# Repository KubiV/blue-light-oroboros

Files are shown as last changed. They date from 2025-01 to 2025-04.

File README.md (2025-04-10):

# blue-light-oroboros

## Úvod
V této práci se zabýváme vývojem externího světelného LED zdroje pro přístroj Oroboros O2k, který slouží pro vysoce přesné monitorování respirační aktivity biologických a biochemických vzorků.

Aplikace pro ovládání LED
*Stroj Oroboros O2k s nasazeným světlem*

## Problém
Stávající světelné zdroje pro Oroboros O2k jsou drahé a u starších modelů již nedostupné. Naším cílem bylo navrhnout cenově dostupnou a modulární alternativu, která by umožnila precizní experimentální podmínky.

## Materiál a metody
Náš systém zahrnuje řídící box s elektronikou založenou na Arduino Leonardo. K ovládání světel je použit rotační enkodér a 3 tlačítka, zatímco desktopová aplikace umožňuje softwarové nastavení PWM signálu (0–255) pro dvě LED diody. LED zdroje s dominantní vlnovou délkou 465 nm jsou integrovány do 3D tištěných pouzder. Experiment proběhl s bilirubinem rozpuštěným v BSA, kdy fotooxidační reakce bilirubinu (na lumirubin a biliverdinové deriváty) vedly k měření spotřeby kyslíku.

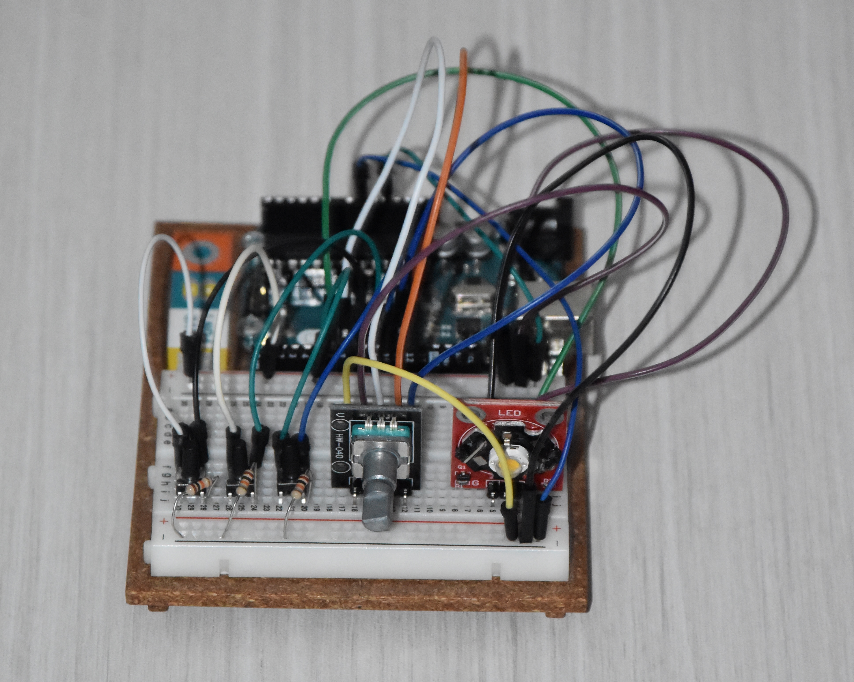
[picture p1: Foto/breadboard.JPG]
První prototyp

*První verze zapojení na nepájivém poli*

Protodeska
*Finální zapojení na prototypové desce*

## Technický popis
Projekt využívá Arduino Leonardo pro řízení dvou LED diod, s PWM regulací a jednoduchým ovládáním pomocí enkodéru a tlačítek. Firmware na řídícím čipu přijímá sériové příkazy pro nastavení jasu jednotlivých LED. Uživatelská aplikace, vyvinutá v Pythonu s knihovnou PyQt5, umožňuje ovládání LED přes grafické rozhraní se samostatnými i synchronizovanými časovači, sliderem a textovým vstupem. Modularita hardwaru umožňuje rozšíření o další zdroje s různými vlnovými délkami.

Finální box
*Finální box s možností připojení dvou LED světel*

## Výsledky
Vyvinutý systém umožňuje individuální i synchronizované ovládání obou LED světel, včetně časovačů pro přesné nastavení trvání osvětlení. Software poskytuje interaktivní slider, tlačítka předvoleb a možnost zadat konkrétní hodnoty jasu, což vede ke spolehlivému monitorování spotřeby kyslíku a k analýze fotoproduktů.

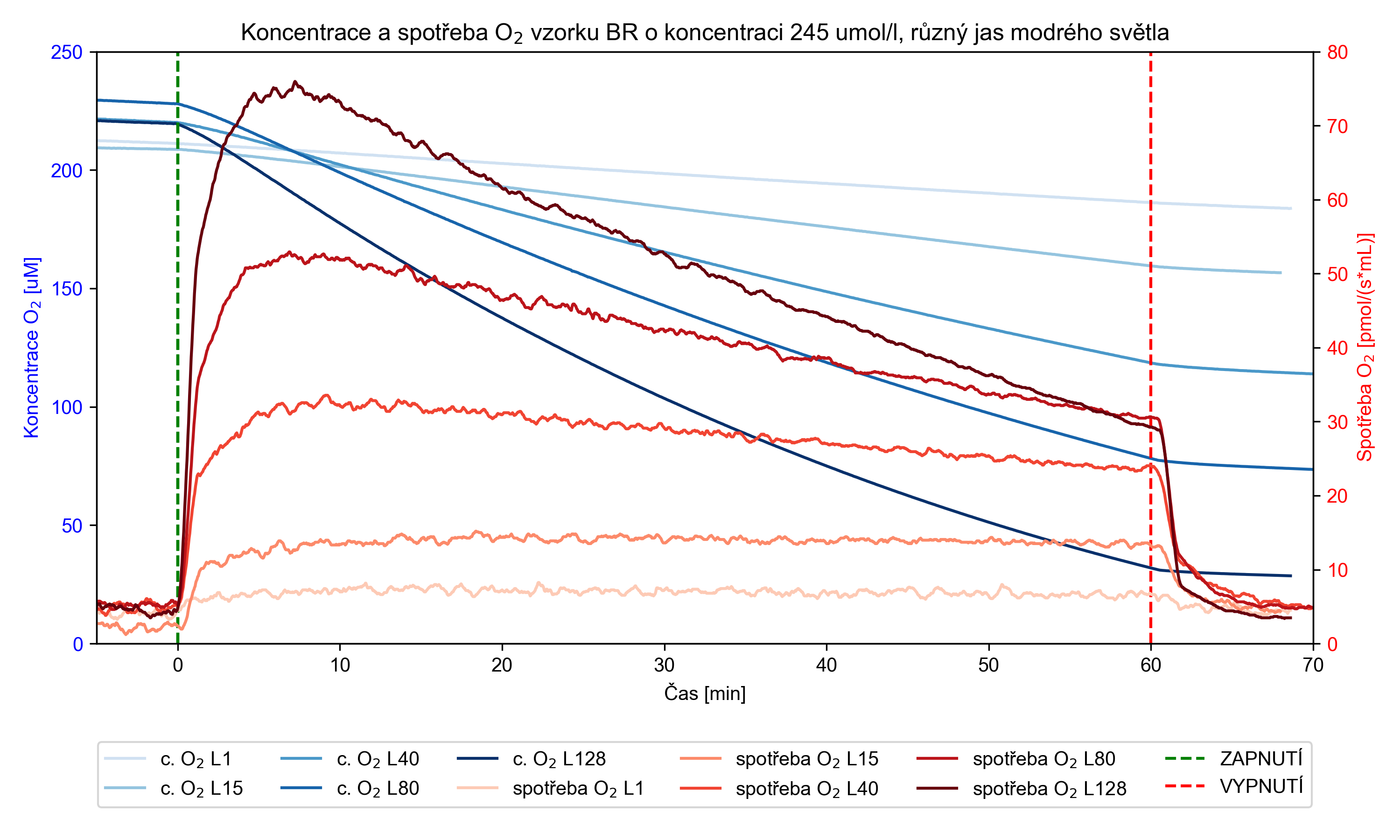
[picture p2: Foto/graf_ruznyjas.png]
Různý jas světla

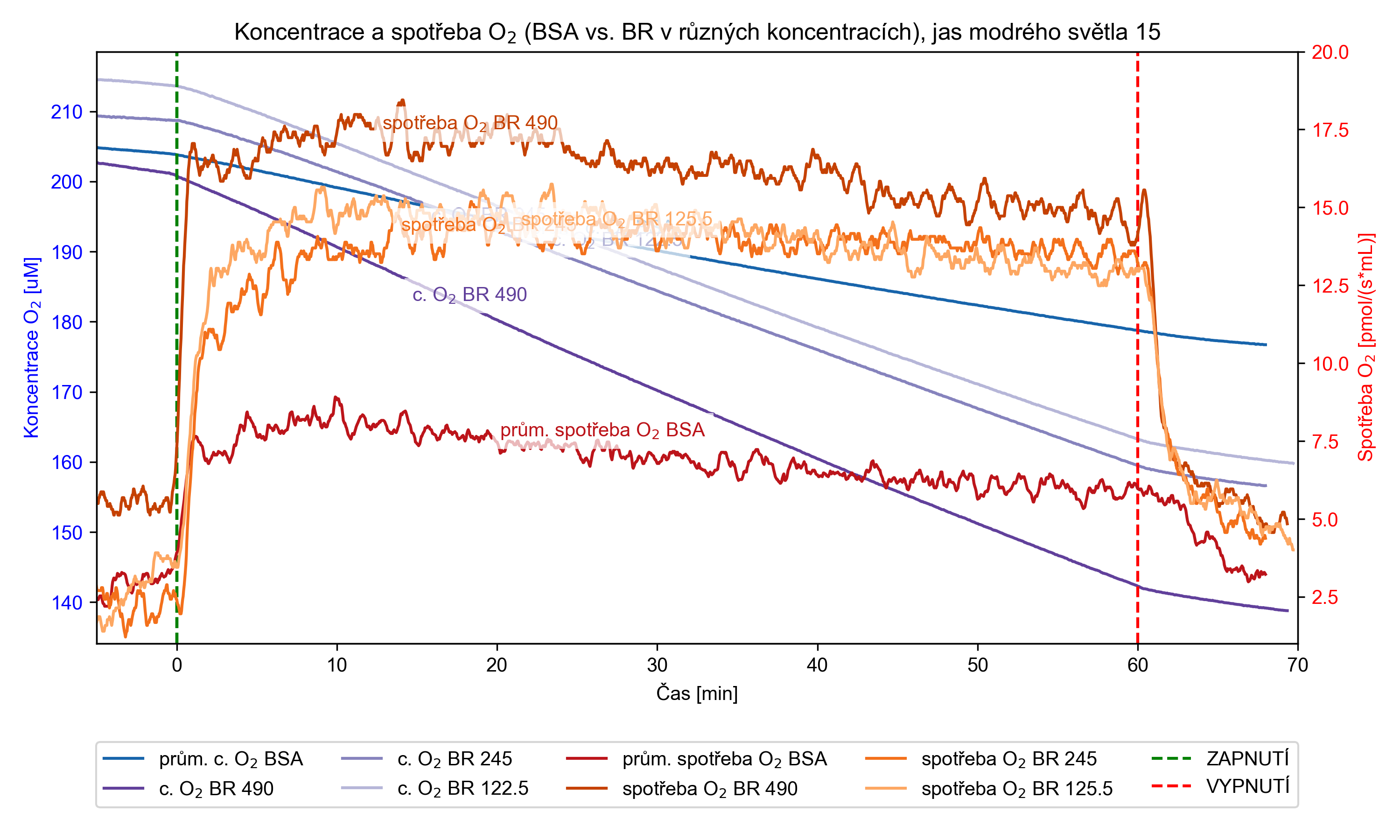
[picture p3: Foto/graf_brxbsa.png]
Různé koncentrace BR

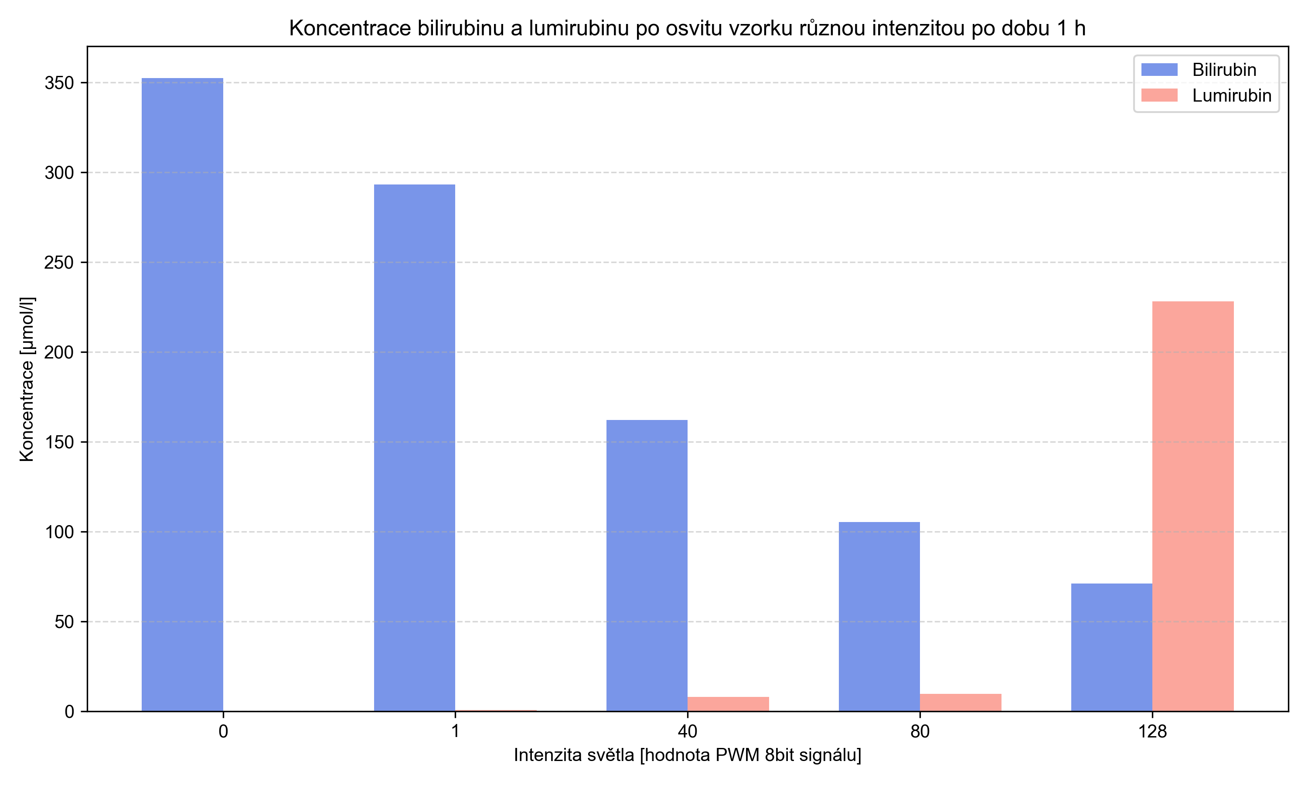
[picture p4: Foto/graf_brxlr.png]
Koncentrace BR a LR

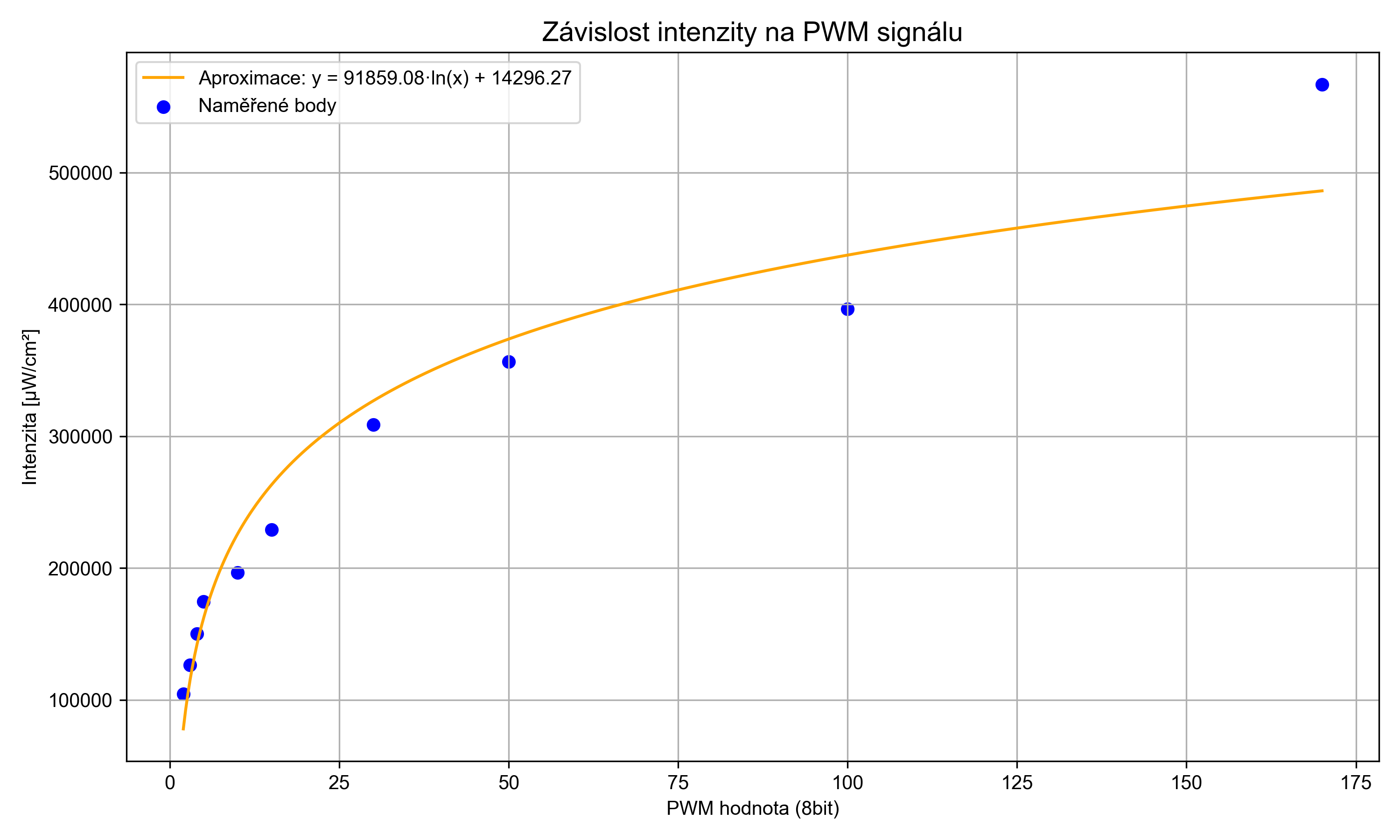
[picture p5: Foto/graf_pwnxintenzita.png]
Intenzita a PWM světelného zdroje


## Závěr a diskuse
Náš LED zdroj představuje praktickou a ekonomickou alternativu k původním řešením. Jeho modularita umožňuje rozšíření o další světelné zdroje s různými vlnovými délkami. Experiment s bilirubinem ukázal, že naše řešení umožňuje precizní kontrolu osvětlení, což výrazně ovlivňuje experimentální podmínky a kvalitu dat.

## Technická dokumentace

### Struktura projektu
```
blue-light-oroboros/
├── requirements.txt         # Seznam závislostí pro Python aplikaci a generování grafů
├── Software/
│   └── SW_Dual/
│       ├── led/
│       │   └── led.ino      # Arduino firmware pro ovládání LED
│       └── led2.py          # Python aplikace pro ovládání LED
├── Data/
│   ├── Graph1/
│   │   └── graph4.py        # Vizualizace dat - koncentrace BR
│   ├── Graph2/
│   │   └── graph1.py        # Vizualizace dat - různé intenzity světla
│   ├── Graph3/
│   │   └── graph1.py        # Vizualizace dat - porovnání BR a LR v různých vzorcích
│   └── Graph4/
│       └── graph1.py        # Vizualizace dat - závislost intenzity a PWM
├── CAD/
│   ├── 3D print/
│   │   └── BlueLight.3mf    # Detaily pro tisk ve formátu 3MF (LED světlo)
│   └── BlueLight.step       # Zdrojový STEP soubor pro 3D model (LED světlo)
└── Docs/
  └── Instrukce.pdf          # Instrukce pro sestavení kryu LED světla
```

### Popis komponent

#### Arduino Firmware (led.ino)
- Ovládání dvou LED zdrojů přes PWM (piny 11 a 3)
- Implementace rotačního enkodéru pro manuální ovládání jasu
- Tři tlačítka pro rychlé předvolby (vypnuto, přepínání LED, maximum)
- Sériová komunikace pro příjem příkazů z PC aplikace

#### Python Aplikace (led2.py)
- GUI aplikace vytvořená v PyQt5
- Ovládání jasu LED pomocí slideru nebo přímého zadání hodnoty
- Implementace časovačů pro každou LED
- Možnost synchronizace obou LED
- Sériová komunikace s Arduino kontrolérem

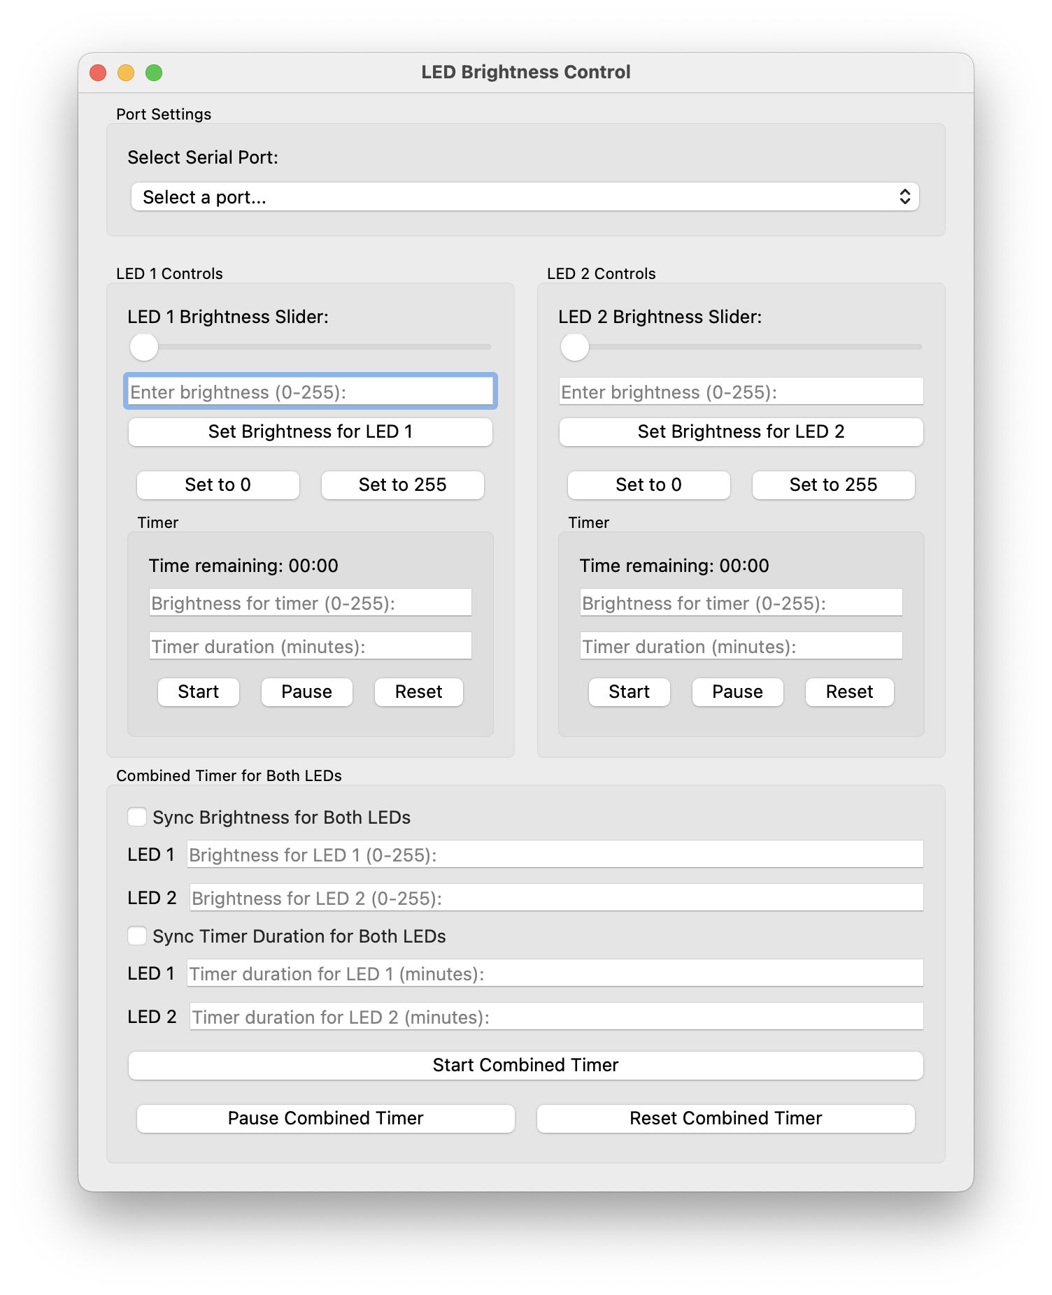
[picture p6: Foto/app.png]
Detail aplikace

*Uživatelské rozhraní aplikace pro ovládání LED světel*

#### Vizualizační skripty
- **graph1.py**: Analýza a vizualizace dat pro různé intenzity osvětlení
- **graph4.py**: Analýza a vizualizace dat pro různé koncentrace bilirubinu

### Hardware
- Arduino Leonardo
- 2x LED dioda (465 nm)
- Rotační enkodér
- 3x tlačítko
- 3D tištěná pouzdra pro LED a řídící box

### Komunikační protokol
- **Příkazy pro Arduino:**
  - `SET1:xxx` - Nastavení jasu LED 1 (xxx = 0-255)
  - `SET2:xxx` - Nastavení jasu LED 2 (xxx = 0-255)
- **Odpovědi z Arduina:**
  - `BRIGHTNESS1:xxx` - Aktuální jas LED 1
  - `BRIGHTNESS2:xxx` - Aktuální jas LED 2

## Literatura
- Oroboros Instruments: https://wiki.oroboros.at/index.php/PB_Light_Source
- Nature Article: https://www.nature.com/articles/s41598-020-61280-z
- Pediatrics: https://publications.aap.org/pediatrics/article/114/1/297/64771/Management-of-Hyperbilirubinemia-in-the-Newborn?autologincheck=redirected

## Poděkování
Děkujeme všem, kteří přispěli svými odbornými znalostmi a podporou k úspěšnému vývoji tohoto projektu.

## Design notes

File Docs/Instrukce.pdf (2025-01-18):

## Sestavení DriverBoxu

1) 3D tisk součástek
- Box
- Cover
- Knob
2) Shromáždění komponent
- LED driver board
- Arduino UNO/Leonardo
- USB kabel
- Rotary encoder
- 3x button
- 3x Rezistor (10 kOhm)
- Kablíky
- Proofboard
- Pinová lišta
- Delší 2 kabely (+ konektor)
- Nejméně 2x M3 matka a šroubek
- Smršťovací bužírky
- Stahovací pásky/lepidlo
3) Stavba obvodu proofboard jako shield desky k Arduino UNO/Leonardo (dle schématu)
4) Usazení shieldu na Arduino plus přidání podpěry kvůli stabilitě při stisku tlačítek
5) Vložení elektroniky do boxu a přišroubování
6) Zavření víka boxu
7) Nasazení knobu na rotary encoder
8) Zajištění víka - stahovací pásky/lepidlo

## Sestavení BlueLight Module

1) 3D tisk komponentů
- Body
- BottomCover
- TopCover

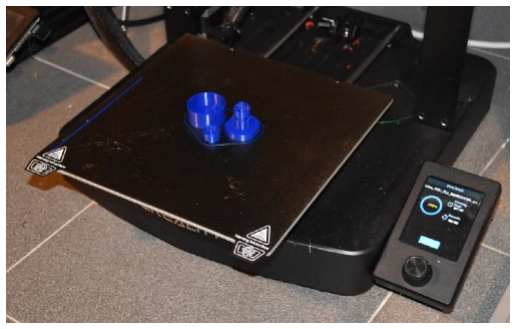
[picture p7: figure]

2) Shromáždění všech součástek
- 2x M2 16 mm šroubky
- 2x M3 10 mm šroubky
- těsnění - 2mm, 14,5 mm/10mm (přibližně)
- 2x kablík (+ konektor - JST SM 2P 2,54 mm)
- 22 mm ALU rod 8 mm průměr
- teplovodivá pasta
- Power LED

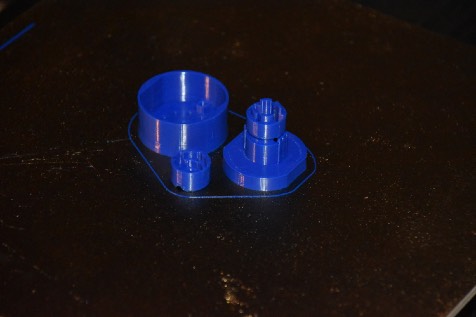
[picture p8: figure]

1 z 5

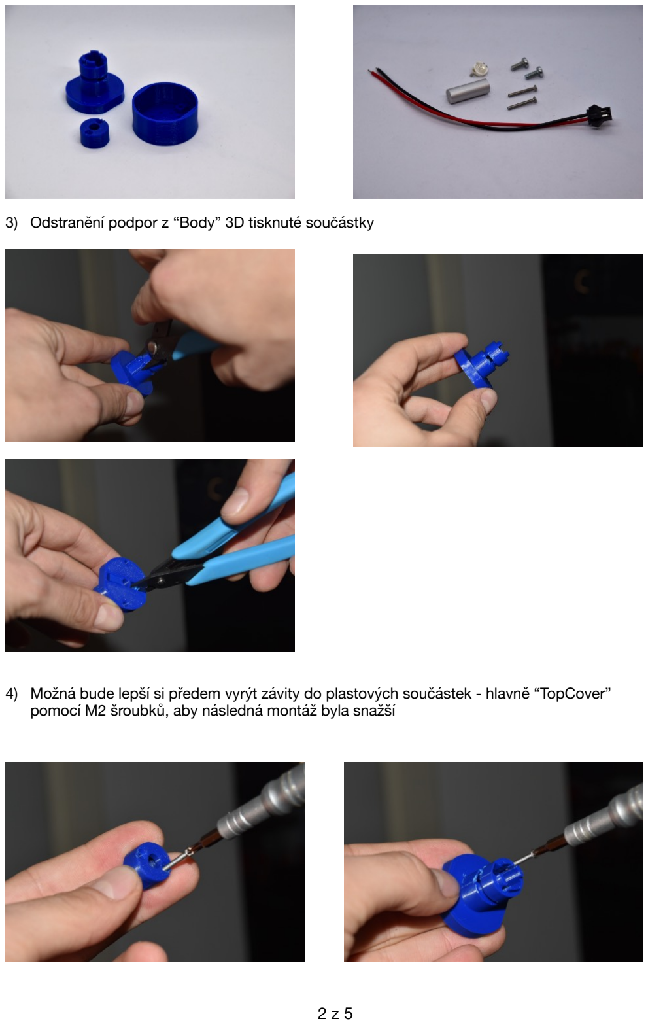
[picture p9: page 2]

3) Odstranění podpor z “Body” 3D tisknuté součástky
4) Možná bude lepší si předem vyrýt závity do plastových součástek - hlavně “TopCover” pomocí M2 šroubků, aby následná montáž byla snažší

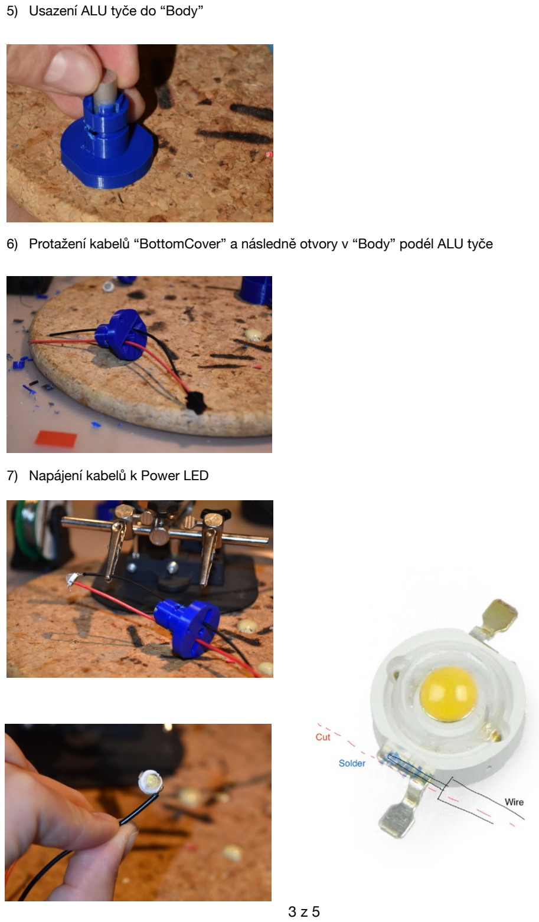
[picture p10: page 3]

5) Usazení ALU tyče do “Body”
6) Protažení kabelů “BottomCover” a následně otvory v “Body” podél ALU tyče
7) Napájení kabelů k Power LED

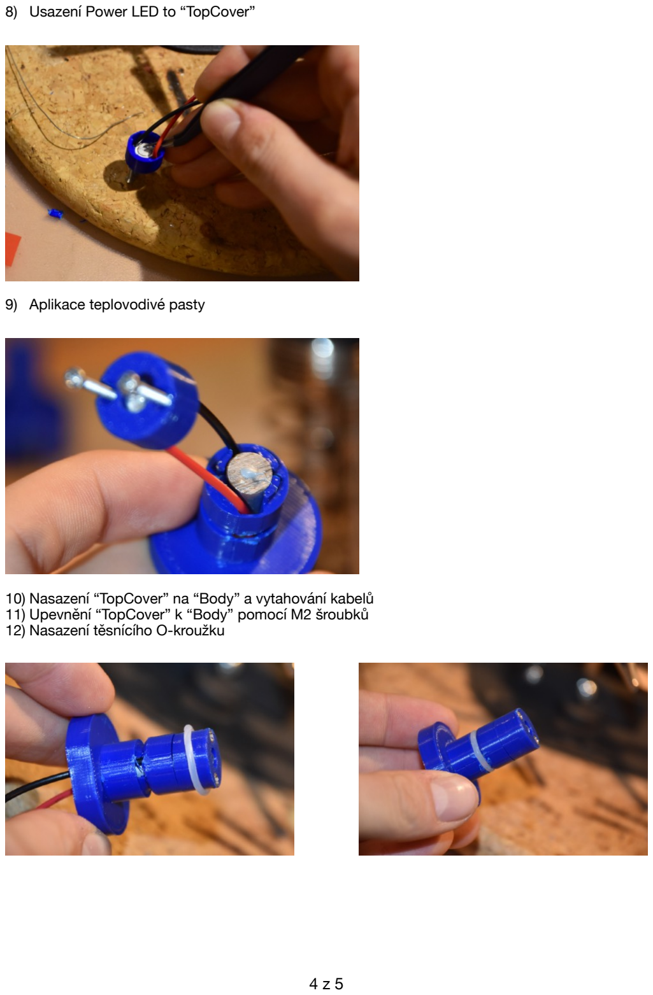
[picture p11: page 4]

8) Usazení Power LED to “TopCover”
9) Aplikace teplovodivé pasty
10) Nasazení “TopCover” na “Body” a vytahování kabelů
11) Upevnění “TopCover” k “Body” pomocí M2 šroubků
12) Nasazení těsnícího O-kroužku

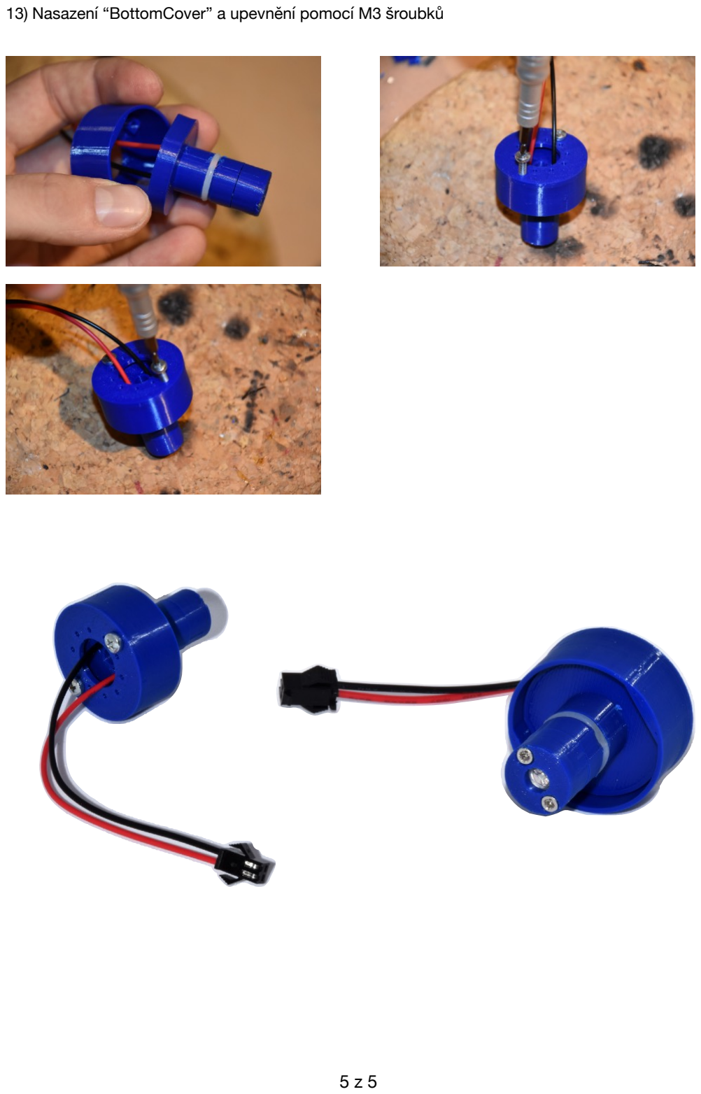
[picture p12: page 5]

13) Nasazení “BottomCover” a upevnění pomocí M3 šroubků

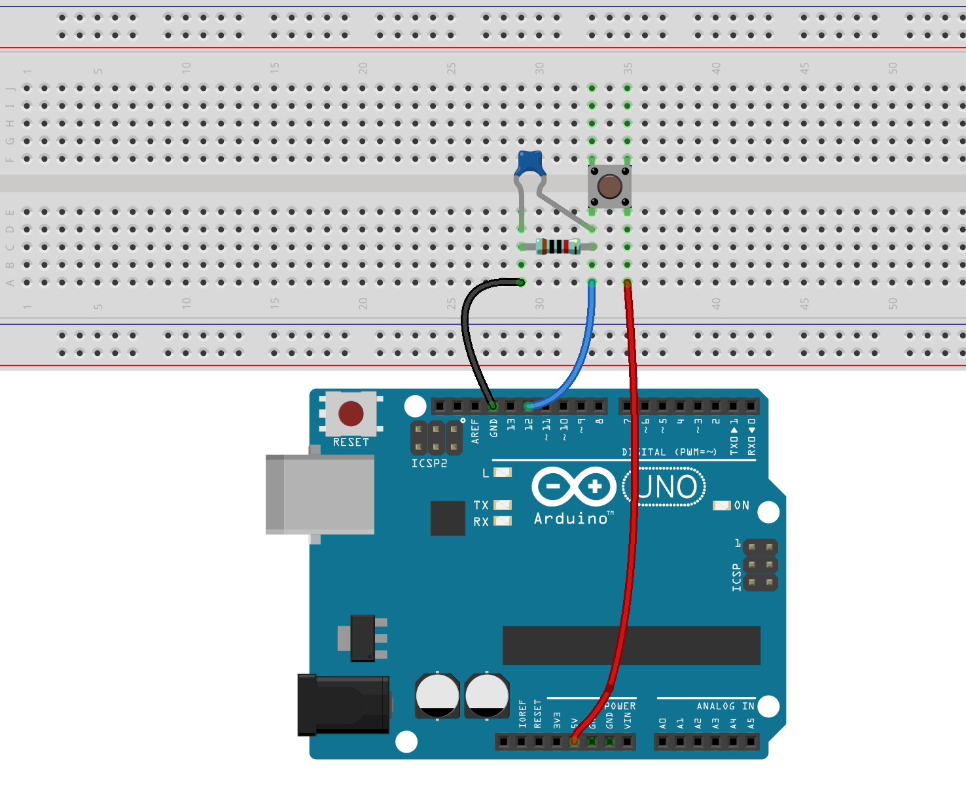
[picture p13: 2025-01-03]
Docs/Datasheets/FFBA2AMJRGOOGF6.png.webp

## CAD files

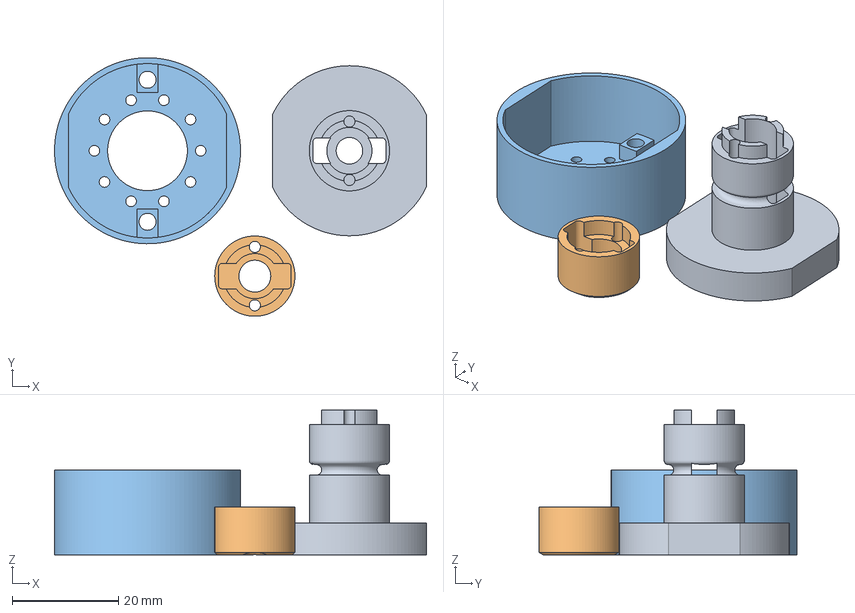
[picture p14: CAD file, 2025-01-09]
CAD/3D print/BlueLight.3mf
70.0 x 48.6 x 27.2 mm
TopCovcer
BottomCover

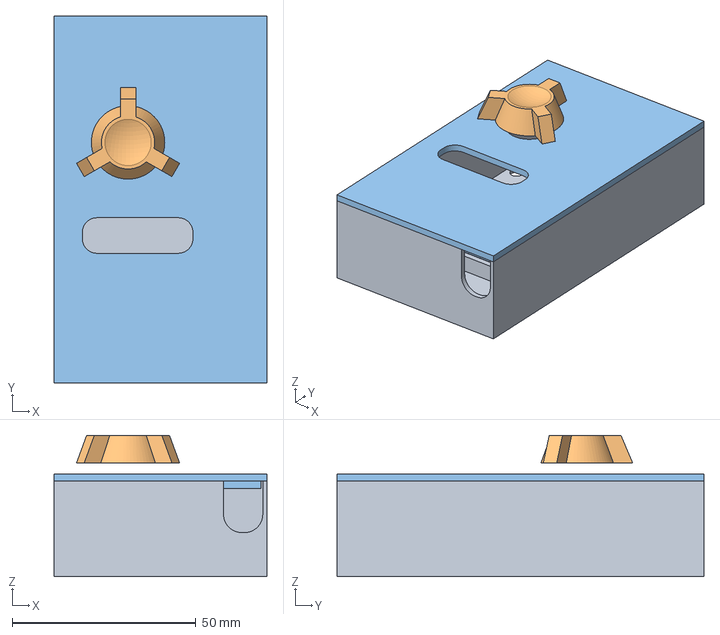
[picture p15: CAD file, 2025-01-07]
CAD/3D print/BlueLight BOX.3mf
58.0 x 100.0 x 38.5 mm

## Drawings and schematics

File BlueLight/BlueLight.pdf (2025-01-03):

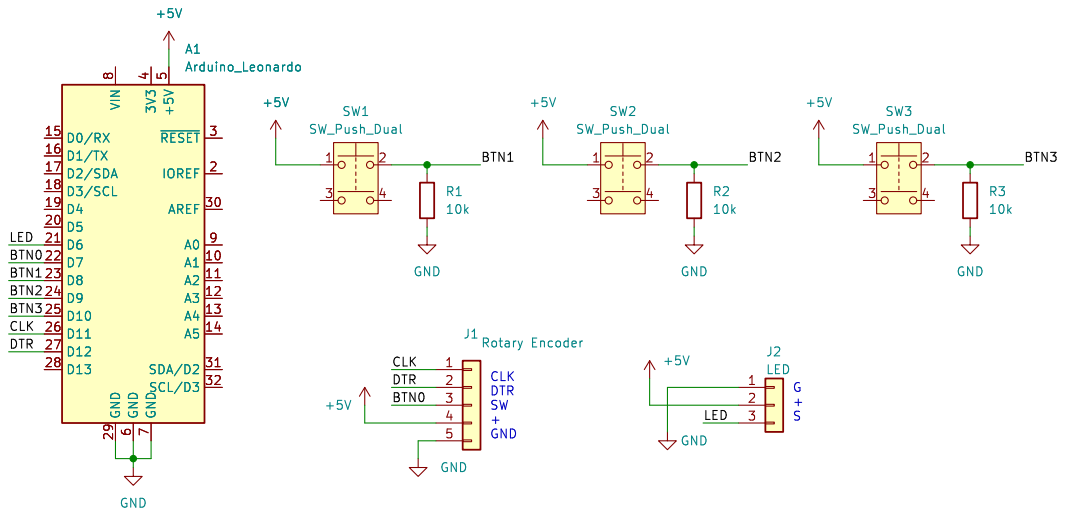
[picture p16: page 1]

Id: 1/1 Title: File: BlueLight.kicad_sch Sheet: /

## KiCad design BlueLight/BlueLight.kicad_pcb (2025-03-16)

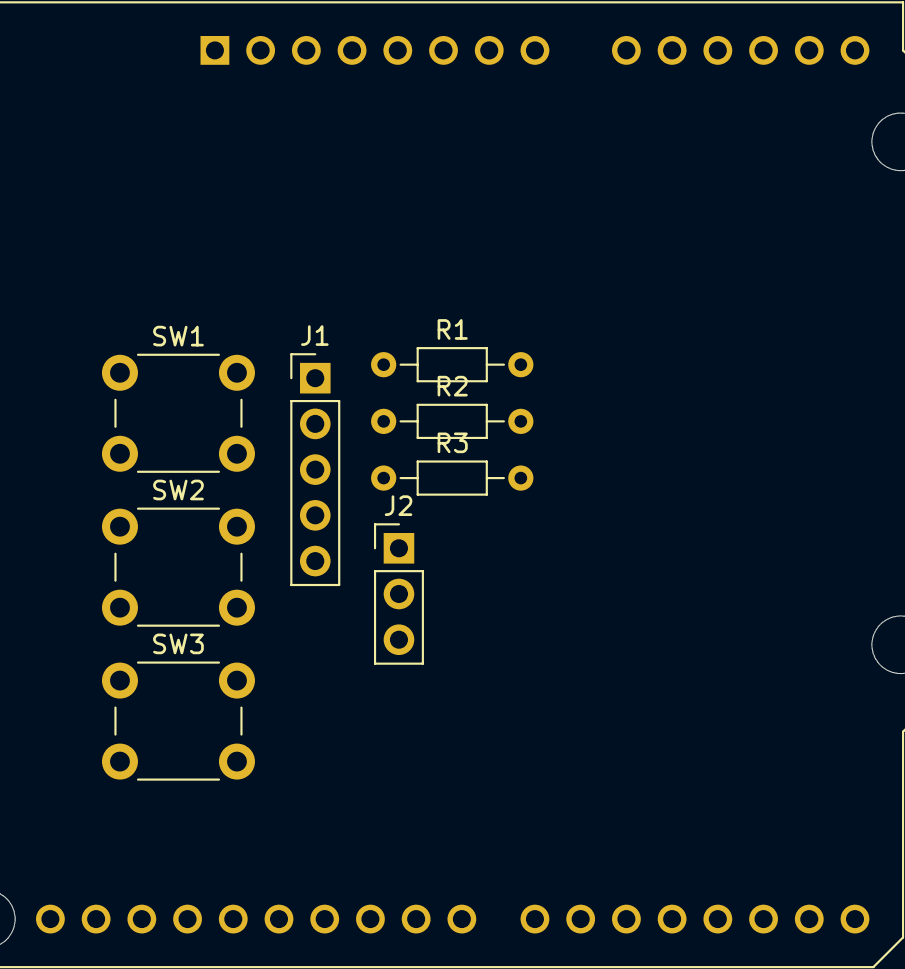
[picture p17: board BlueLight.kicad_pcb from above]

Board: 2 copper layers, 9 parts (0 on the bottom side), 9 nets, no tracks yet.

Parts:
A1: Arduino_Leonardo; Arduino_UNO_R3_WithMountingHoles
J1: Rotary Encoder; PinHeader_1x05_P2.54mm_Vertical
J2: LED; PinHeader_1x03_P2.54mm_Vertical
R1, R2, R3: 10k; R_Axial_DIN0204_L3.6mm_D1.6mm_P7.62mm_Horizontal
SW1, SW2, SW3: SW_Push_Dual; SW_PUSH_6mm

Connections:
+5V: A1.5 (+5V), J1.4, J2.2, SW1.1, SW2.1, SW3.1
/BTN0: A1.22 (D7), J1.3
/BTN1: A1.23 (D8), R1.1, SW1.2
/BTN2: A1.24 (D9), R2.1, SW2.2
/BTN3: A1.25 (D10), R3.1, SW3.2
/CLK: A1.28 (D13), J1.1
/DTR: A1.27 (D12), J1.2
/LED: A1.26 (D11), J2.3
GND: A1.6 (GND), A1.7 (GND), A1.29 (GND), J1.5, J2.1, R1.2, R2.2, R3.2

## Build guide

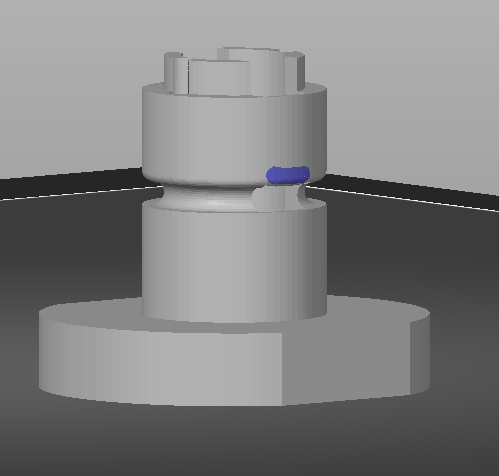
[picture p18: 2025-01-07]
CAD/3D print/Screenshot 2025-01-07 at 22.44.59.png

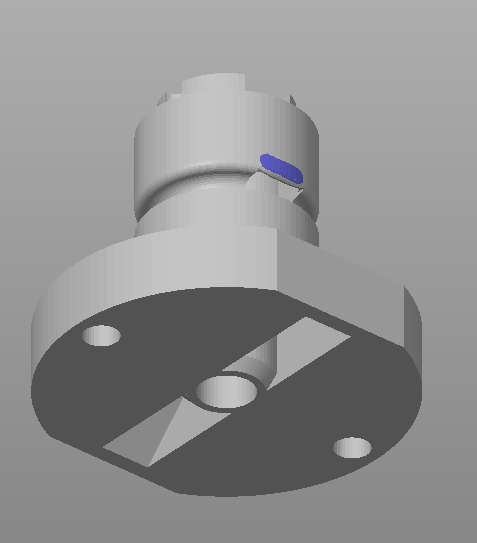
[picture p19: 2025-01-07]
CAD/3D print/Screenshot 2025-01-07 at 22.45.04.png

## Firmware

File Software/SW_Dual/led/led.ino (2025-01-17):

#include <Arduino.h>

// Pin assignments
#define LED_1_PIN 11
#define LED_2_PIN 3
#define CLK 13
#define DT 12
#define SW 7
#define BUTTON1_PIN 8
#define BUTTON2_PIN 9
#define BUTTON3_PIN 10

// Variables
int brightness1 = 0;         // Brightness for LED 1 (0-255)
int brightness2 = 0;         // Brightness for LED 2 (0-255)
int encoderValue = 0;
int lastStateCLK = LOW;
int currentStateCLK = LOW;
bool brightnessChanged = false;
bool activeLED = 1;          // 1 for LED_1, 0 for LED_2

// Setup
void setup() {
  Serial.begin(9600);
  Serial.println("BRIGHTNESS1:0");
  Serial.println("BRIGHTNESS2:0");

  // Pin modes
  pinMode(LED_1_PIN, OUTPUT);
  pinMode(LED_2_PIN, OUTPUT);
  pinMode(CLK, INPUT);
  pinMode(DT, INPUT);
  pinMode(SW, INPUT_PULLUP);
  pinMode(BUTTON1_PIN, INPUT);
  pinMode(BUTTON2_PIN, INPUT);
  pinMode(BUTTON3_PIN, INPUT);

  // Initial state of encoder
  lastStateCLK = digitalRead(CLK);
}

// Main loop
void loop() {
  // --- Encoder Rotation ---
  currentStateCLK = digitalRead(CLK);
  if (currentStateCLK != lastStateCLK) {
    if (digitalRead(DT) != currentStateCLK) {
      if (activeLED) {
        brightness1 += 5;
      } else {
        brightness2 += 5;
      }
    } else {
      if (activeLED) {
        brightness1 -= 5;
      } else {
        brightness2 -= 5;
      }
    }

    brightness1 = constrain(brightness1, 0, 255);
    brightness2 = constrain(brightness2, 0, 255);
    brightnessChanged = true;
  }
  lastStateCLK = currentStateCLK;

  // --- Button Press ---
  if (digitalRead(BUTTON1_PIN) == HIGH) {
    if (activeLED) {
      brightness1 = 0;
    } else {
      brightness2 = 0;
    }
    brightnessChanged = true;
  }
  if (digitalRead(BUTTON2_PIN) == HIGH) {
    activeLED = !activeLED; // Toggle active LED
    delay(200);             // Debounce delay
  }
  if (digitalRead(BUTTON3_PIN) == HIGH) {
    if (activeLED) {
      brightness1 = 255;
    } else {
      brightness2 = 255;
    }
    brightnessChanged = true;
  }

  // --- Update LED brightness ---
  if (brightnessChanged) {
    analogWrite(LED_1_PIN, brightness1);
    analogWrite(LED_2_PIN, brightness2);
    Serial.println(String("BRIGHTNESS1:") + brightness1);
    Serial.println(String("BRIGHTNESS2:") + brightness2);
    brightnessChanged = false;
  }

  // --- Handle Serial Communication ---
  if (Serial.available()) {
    String input = Serial.readStringUntil('\n');
    if (input.startsWith("SET1:")) {
      brightness1 = constrain(input.substring(5).toInt(), 0, 255);
      analogWrite(LED_1_PIN, brightness1);
      Serial.println(String("BRIGHTNESS1:") + brightness1);
    }
    if (input.startsWith("SET2:")) {
      brightness2 = constrain(input.substring(5).toInt(), 0, 255);
      analogWrite(LED_2_PIN, brightness2);
      Serial.println(String("BRIGHTNESS2:") + brightness2);
    }
  }
}

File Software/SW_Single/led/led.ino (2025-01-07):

#include <Arduino.h>

// Pin assignments
#define LED_PIN 11
#define CLK 13
#define DT 12
#define SW 7
#define BUTTON1_PIN 8
#define BUTTON2_PIN 9
#define BUTTON3_PIN 10

// Variables
int brightness = 0;         // Current brightness level (0-255)
int encoderValue = 0;
int lastStateCLK = LOW;
int currentStateCLK = LOW;
bool brightnessChanged = false;

// Setup
void setup() {
  Serial.begin(9600);
  Serial.println(String("BRIGHTNESS:") + brightness);
  
  // Pin modes
  pinMode(LED_PIN, OUTPUT);
  pinMode(CLK, INPUT);
  pinMode(DT, INPUT);
  pinMode(SW, INPUT_PULLUP);
  pinMode(BUTTON1_PIN, INPUT);
  pinMode(BUTTON2_PIN, INPUT);
  pinMode(BUTTON3_PIN, INPUT);

  // Initial state of encoder
  lastStateCLK = digitalRead(CLK);
}

// Main loop
void loop() {
  // --- Encoder Rotation ---
  currentStateCLK = digitalRead(CLK);
  if (currentStateCLK != lastStateCLK) {
    if (digitalRead(DT) != currentStateCLK) {
      brightness += 5;
    } else {
      brightness -= 5;
    }
    brightness = constrain(brightness, 0, 255); // Ensure brightness is within 0-255
    brightnessChanged = true;
  }
  lastStateCLK = currentStateCLK;

  // --- Button Press ---
  if (digitalRead(BUTTON1_PIN) == HIGH) {
    brightness = 0;
    brightnessChanged = true;
  }
  if (digitalRead(BUTTON2_PIN) == HIGH) {
    brightness = 128;
    brightnessChanged = true;
  }
  if (digitalRead(BUTTON3_PIN) == HIGH) {
    brightness = 255;
    brightnessChanged = true;
  }

  // --- Update LED brightness ---
  if (brightnessChanged) {
    analogWrite(LED_PIN, brightness);
    Serial.println(String("BRIGHTNESS:") + brightness);
    brightnessChanged = false;
  }

  // --- Handle Serial Communication ---
  if (Serial.available()) {
    String input = Serial.readStringUntil('\n');
    if (input.startsWith("SET:")) {
      brightness = constrain(input.substring(4).toInt(), 0, 255); // Ensure brightness is within 0-255
      analogWrite(LED_PIN, brightness);
      Serial.println(String("BRIGHTNESS:") + brightness);
    }
  }
}

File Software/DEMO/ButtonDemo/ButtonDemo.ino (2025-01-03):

const int buttonPin1 = 8;
const int buttonPin2 = 9;
const int buttonPin3 = 10;

int buttonState1 = 0;
int buttonState2 = 0;
int buttonState3 = 0;

void setup() {
  Serial.begin(9600);
  pinMode(buttonPin1, INPUT); // Keep as INPUT for external pull-down
  pinMode(buttonPin2, INPUT);
  pinMode(buttonPin3, INPUT);
}

void loop() {
  buttonState1 = digitalRead(buttonPin1);
  buttonState2 = digitalRead(buttonPin2);
  buttonState3 = digitalRead(buttonPin3);

  if (buttonState1 == HIGH) {
    Serial.println("Button 1 pressed");
  }
  if (buttonState2 == HIGH) {
    Serial.println("Button 2 pressed");
  }
  if (buttonState3 == HIGH) {
    Serial.println("Button 3 pressed");
  }
  delay(100);
}

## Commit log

2025-01-07 new app
    timer added
    [BlueLight.3mf, BlueLight.kicad_pcb, BlueLight.kicad_sch]
2025-01-07 cad
    cad files added
    [BlueLight BOX.3mf, BlueLight.3mf]
2025-01-17 doule version init
    [BlueLight.kicad_sch]
2025-03-16 readme + data
    [1-exp_blue.light.xlsx, BR123.csv, BR245.csv, BR490.csv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]
2025-04-04 end products graph
    [HPLCdataBRLR.csv]
2025-04-08 case sensitive
2025-04-09 new graph
    [PWMtoIntensity.csv]
